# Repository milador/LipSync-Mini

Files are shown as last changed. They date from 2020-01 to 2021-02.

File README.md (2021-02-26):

# LipSync-Mini

Lipsync with updated electronics (Adafruit ItsyBitsy and RGB LED)

<p align="center">
LipSync Logo
</p>

The LipSync is an assistive technology device developed by <a href="https://www.makersmakingchange.com/" download target="_blank">MakersMakingChange</a> (An initiative by the <a href="https://www.neilsquire.ca/" download target="_blank">Neil Squire Society</a>) which allows quadriplegics and other people with limited hand use the ability to use touchscreen mobile devices by manipulation of a mouth-operated joystick with integrated sip and puff controls. 

<p align="center">
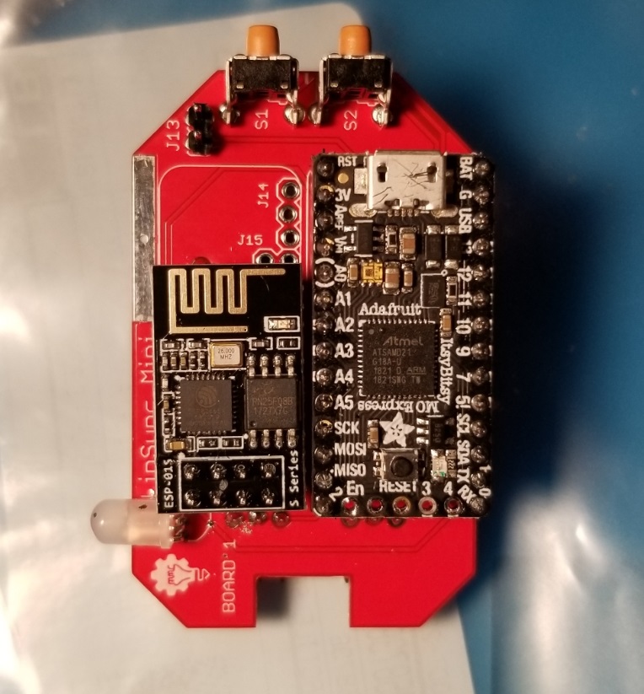
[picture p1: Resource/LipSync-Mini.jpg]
LipSync Logo

</p>

## Main LipSync github repository 

The LipSync Mini project is based on the <a href="https://github.com/makersmakingchange/LipSync" download target="_blank">LipSync</a>

## Changes Made

1. Dual color Led replaced by RGB addressable 
2. Arduino Micro replaced by Adafruit ItsyBitsy M0 (More memory and power)
3. Transistor and header pins for bluetooth module removed 
4. ItsyBitsy nRF52840 Express with bluetooth 5.0 is used for bluetooth version (Adafruit ItsyBitsy M0 replaced by ItsyBitsy nRF52840 Express)
5. Option to add ESP8266 Wifi Module to enable controlling IOT devices 
6. Option to add internal battery charger
7. Option to use internal input 3.5mm jack switch 
8. Option to replace sip and puff module with bite switch PCB

## License 

### MIT License

Copyright (c) 2020 Milador

Permission is hereby granted, free of charge, to any person obtaining a copy of this software and associated documentation files (the "Software"), to deal in the Software without restriction, including without limitation the rights to use, copy, modify, merge, publish, distribute, sublicense, and/or sell copies of the Software, and to permit persons to whom the Software is furnished to do so, subject to the following conditions:

The above copyright notice and this permission notice shall be included in all copies or substantial portions of the Software.

THE SOFTWARE IS PROVIDED "AS IS", WITHOUT WARRANTY OF ANY KIND, EXPRESS OR IMPLIED, INCLUDING BUT NOT LIMITED TO THE WARRANTIES OF MERCHANTABILITY, FITNESS FOR A PARTICULAR PURPOSE AND NONINFRINGEMENT. IN NO EVENT SHALL THE AUTHORS OR COPYRIGHT HOLDERS BE LIABLE FOR ANY CLAIM, DAMAGES OR OTHER LIABILITY, WHETHER IN AN ACTION OF CONTRACT, TORT OR OTHERWISE, ARISING FROM, OUT OF OR IN CONNECTION WITH THE SOFTWARE OR THE USE OR OTHER DEALINGS IN THE SOFTWARE.

<p align="center">
MIT License
</p>

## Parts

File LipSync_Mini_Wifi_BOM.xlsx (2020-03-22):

Qty | Component | Component name (August 12, 2019) | Manufacturer | COO | MPN | SKU | SKU | SKU | SKU | SKU | SKU | SKU | SKU | URL ( Canada ) | URL ( United States )
 |  |  |  |  |  | Digi-Key | Mouser | Qosina | Cole-Parmer | Lee Spring | U.S. Plastic Corp. | B&H Photo | Amazon
1 | Required | ItsyBitsy M0 Express | Adafruit Industries LLC | USA | "3727" | 1528-2554-ND | 485-3727 |  |  |  |  |  |  | https://www.digikey.ca/en/products/detail/adafruit-industries-llc/3727/8346575 | https://www.digikey.com/product-detail/en/arduino/A000053/1050-1066-ND
1 | Required | ESP8266 Wifi Module | SparkFun Electronics | USA | WRL-13678 | 1568-1235-ND |  |  |  |  |  |  |  | https://www.digikey.ca/product-detail/en/sparkfun-electronics/WRL-13678/1568-1235-ND/
1 | Required | 8 Position Header Connector Through Hole | Sullins | Taiwan | PPPC042LFBN-RC | S7107-ND |  |  |  |  |  |  |  | https://www.digikey.ca/product-detail/en/sullins-connector-solutions/PPPC042LFBN-RC/S7107-ND
2 | Required | Right Angle Push Button | Würth Elektronik | China | "431256058736" | 431256058736-ND |  |  |  |  |  |  |  | http://www.digikey.ca/product-detail/en/wurth-electronics-inc/431256058736/431256058736-ND | https://www.digikey.com/product-detail/en/wurth-electronics-inc/431256058736/431256058736-ND
4 | Required | 10k Ohm 1/4W Mini Axial Through-Hole Resistor | Stackpole Electronics | China | CFM14JT10K0 | S10KQCT-ND |  |  |  |  |  |  |  | https://www.digikey.ca/product-detail/en/stackpole-electronics-inc/CFM14JT10K0/S10KQCT-ND/ | https://www.digikey.com/product-detail/en/stackpole-electronics-inc/CFM14JT10K0/S10KQCT-ND/
1 | Required | Pressure Transducer | NXP Semiconductors | Malaysia | MP3V5010DP | MP3V5010DP-ND | 841-MP3V5010DP |  |  |  |  |  |  | https://www.digikey.ca/product-detail/en/nxp-usa-inc/MP3V5010DP/MP3V5010DP-ND | https://www.digikey.com/product-detail/en/freescale-semiconductor-nxp/MPXV7002DPT1/MPXV7002DPT1CT-ND
1 | Required | 0.01 uF Ceramic Through-Hole Radial Capacitor | KEMET | Mexico | C315C103K5R5TA | 399-4148-ND | 80-C315C103K5R |  |  |  |  |  |  | http://www.digikey.ca/product-detail/en/kemet/C315C103K5R5TA7303/399-9858-1-ND | http://www.digikey.com/product-detail/en/kemet/C315C103K5R5TA7303/399-9858-1-ND
1 | Required | 1.0 uF Ceramic Through-Hole Radial Capacitor | KEMET | Mexico | C315C105K3R5TA | 399-9714-ND | 80-C315C105K3R |  |  |  |  |  |  | http://www.digikey.ca/product-detail/en/kemet/C315C105K3R5TA/399-9714-ND | http://www.digikey.com/product-detail/en/kemet/C315C105K3R5TA/399-9714-ND
1 | Required | 470 pF Ceramic Through-Hole Radial Capacitor | KEMET | Mexico | C315C471K5R5TA | 399-9740-ND | 80-C315C471K5R |  |  |  |  |  |  | http://www.digikey.ca/product-detail/en/kemet/C315C471K5R5TA/399-9740-ND | http://www.digikey.com/product-detail/en/kemet/C315C471K5R5TA/399-9740-ND
2 | Required | 14-Position Straight Female Through-Hole Headers | Sullins | Taiwan | PPPC141LFBN-RC | S7047-ND |  |  |  |  |  |  |  | https://www.digikey.ca/product-detail/en/sullins-connector-solutions/PPPC141LFBN-RC/S7047-ND | http://www.digikey.com/product-detail/en/sullins-connector-solutions/PPPC171LFBN-RC/S7050-ND
2 | Required | 3-Position Right Angle Male Through-Hole Header | Molex | Mexico | 22-05-2031 | WM4101-ND |  |  |  |  |  |  |  | https://www.digikey.ca/product-detail/en/molex-connector-corporation/22-05-2031/WM4101-ND/ | https://www.digikey.com/product-detail/en/molex-connector-corporation/22-05-2031/WM4101-ND/ (https://www.digikey.ca/product-detail/en/molex-connector-corporation/22-05-2031/WM4101-ND/)
2 | Required | 3-Position Straight Female Through-Hole Header | Preci-Dip | Switzerland | 801-87-003-10-001101 | 1212-1180-ND |  |  |  |  |  |  |  | https://www.digikey.ca/product-detail/en/preci-dip/801-87-003-10-001101/1212-1180-ND | https://www.digikey.com/product-detail/en/preci-dip/801-87-003-10-001101/1212-1180-ND (https://www.digikey.ca/product-detail/en/preci-dip/801-87-003-10-001101/1212-1180-ND)
2 | Required | 4-Position Straight Female Through-Hole Header | Sullins | Taiwan | PPPC041LFBN-RC | S7037-ND |  |  |  |  |  |  |  | http://www.digikey.ca/product-detail/en/sullins-connector-solutions/PPPC041LFBN-RC/S7037-ND | https://www.digikey.com/product-detail/en/sullins-connector-solutions/PPPC041LFBN-RC/S7037-ND
1 | Required | 40-Position Breakaway Straight Male Through-Hole Headers | Sullins | Taiwan | PRPC040SAAN-RC | S1011EC-40-ND |  |  |  |  |  |  |  | http://www.digikey.ca/product-detail/en/sullins-connector-solutions/PRPC040SAAN-RC/S1011EC-40-ND | http://www.digikey.com/product-detail/en/sullins-connector-solutions/PRPC040SAAN-RC/S1011EC-40-ND
1 | Required | Addressable Lighting - 5 LED Discrete Serial | SparkFun Electronics | USA | COM-12986 | 1568-1213-ND |  |  |  |  |  |  |  | https://www.digikey.ca/en/products/detail/sparkfun-electronics/COM-12986/5673799 | https://www.digikey.com/product-detail/en/everlight-electronics-co-ltd/MV5437/1080-1109-ND/2675601 (https://www.digikey.ca/product-detail/en/everlight-electronics-co-ltd/MV5437/1080-1109-ND/2675600)
1 | Required | Jumper Shunt Connector | Sullins | Taiwan | SSC02SYAN | S9002-ND |  |  |  |  |  |  |  | https://www.digikey.ca/product-detail/en/sullins-connector-solutions/SPC02SYAN/S9002-ND | https://www.digikey.com/product-detail/en/sullins-connector-solutions/SPC02SYAN/S9002-ND (https://www.digikey.ca/product-detail/en/sullins-connector-solutions/SPC02SYAN/S9002-ND)
1 | Required | 6-Position Straight Female Through-Hole Header | Sullins | Taiwan | PPPC061LFBN-RC | S7039-ND |  |  |  |  |  |  |  | https://www.digikey.ca/product-detail/en/sullins-connector-solutions/PPPC061LFBN-RC/S7039-ND | https://www.digikey.com/product-detail/en/sullins-connector-solutions/PPPC061LFBN-RC/S7039-ND (https://www.digikey.ca/product-detail/en/sullins-connector-solutions/PPPC061LFBN-RC/S7039-ND)
1 | Required | Sip and Puff Mouthpiece | Qosina | USA | "80102" |  |  | "80102" |  |  |  |  |  | https://www.qosina.com/stepped-male-luer-lock-connector-80102 | https://www.qosina.com/stepped-male-luer-lock-connector-80102
1 | Required | Filter PTFE Hydrophobic 17 mm, 0.2 Micron | Qosina | USA | "28213" |  |  | "28213" |  |  |  |  |  | http://www.qosina.com/hydrophobic-filter-with-female-luer-lock-inlet-male-luer-lock-outlet-28213 | http://www.qosina.com/hydrophobic-filter-with-female-luer-lock-inlet-male-luer-lock-outlet-28213
1 | Required | Luer Lock Fitting | Cole-Parmer | USA | RK-45508-32 |  |  |  | RK-45508-32 |  |  |  |  | https://www.coleparmer.ca/i/cole-parmer-female-luer-bulkhead-1-4-28-unf-thread-to-3-32-hose-barb-pp-25-pk/4550832 | https://www.coleparmer.ca/i/cole-parmer-female-luer-bulkhead-1-4-28-unf-thread-to-3-32-hose-barb-pp-25-pk/4550832
4 | Required | Force Resistive Sensor | Interlink Electronics | China | 30-49649 | 1027-1000-ND |  |  |  |  |  |  |  | http://www.digikey.ca/product-detail/en/interlink-electronics/30-49649/1027-1000-ND | http://www.digikey.com/product-detail/en/interlink-electronics/30-49649/1027-1000-ND
4 | Required | Screws Phillips Head M3 | Essentra Components | Taiwan | NMS-308 | RP809-ND |  |  |  |  |  |  |  | https://www.digikey.ca/product-detail/en/essentra-components/NMS-308/RP809-ND | https://www.digikey.com/product-detail/en/essentra-components/NMS-308/RP809-ND (https://www.digikey.ca/product-detail/en/essentra-components/NMS-308/RP809-ND)
6 | Required | Compression Spring | Lee Spring | China | LC 016C 03 S |  |  |  |  | LC 016C 03 S |  |  |  | https://www.leespring.com/compression-springs?search=LC016C03S | https://www.leespring.com/compression-springs?search=LC016C03S
2 | Required | Standoff M3 10mm | Keystone | USA | "25501" | 36-25501-ND | 534-25501 |  |  |  |  |  |  | http://www.digikey.ca/product-detail/en/keystone-electronics/25501/36-25501-ND/ | http://www.digikey.com/product-detail/en/keystone-electronics/25501/36-25501-ND/
2 | Required | Standoff M3 15mm | Keystone | USA | "25503" | 36-25503-ND | 534-25503 |  |  |  |  |  |  | http://www.digikey.ca/product-detail/en/keystone-electronics/25503/36-25503-ND/ | http://www.digikey.com/product-detail/en/keystone-electronics/25503/36-25503-ND/ (http://www.digikey.ca/product-detail/en/keystone-electronics/25503/36-25503-ND/)
1 | Required | Luer Lock Nut | Cole-Parmer | USA | 45509-04 |  |  |  | 45509-04 |  |  |  |  | https://www.coleparmer.ca/i/cole-parmer-panel-mount-lock-nut-1-4-28-unf-black-nylon-25-pk/4550904 | https://www.coleparmer.ca/i/cole-parmer-panel-mount-lock-nut-1-4-28-unf-black-nylon-25-pk/4550904
4 | Required | Bumper | 3M | USA | SJ-5003 (BLACK) | SJ5003-0-ND | 517-SJ-5003BK |  |  |  |  |  |  | https://www.mouser.ca/ProductDetail/3M-Electronic-Specialty/SJ-5003-BLACK?qs=sGAEpiMZZMvlOED0T0kTWubpGv7E7tyx | https://www.digikey.com/product-detail/en/3m/SJ-5003-(BLACK)/SJ5003-0-ND/102574 (https://www.digikey.ca/product-detail/en/3m/SJ-5003-(BLACK)/SJ5003-0-ND/102573)
4 | Required | Nut M3 | Keystone Electronics | Taiwan | 4708 | 36-4708-ND |  |  |  |  |  |  |  | https://www.digikey.ca/product-detail/en/keystone-electronics/4708/36-4708-ND/4499301 | https://www.digikey.com/product-detail/en/keystone-electronics/4708/36-4708-ND/4499301
1 | Required | Tubing Tygon 3350 3/32" ID x 45mm | Tygon® | USA | "57289" |  |  |  |  |  | "57289" |  |  | http://www.usplastic.com/catalog/item.aspx?itemid=31562&catid=864 | http://www.usplastic.com/catalog/item.aspx?itemid=31562&catid=864
1 | Required | Light Pipe | Dialight | Malaysia | 51513030250F | 350-3746-ND | 645-515-1303-0250F |  |  |  |  |  |  | http://www.mouser.com/search/ProductDetail.aspx?r=645-515-1303-0250F | http://www.mouser.com/search/ProductDetail.aspx?r=645-515-1303-0250F
1 | Required | Threaded Insert 5/8”-27 | WindTech | USA | M-11 |  |  |  |  |  |  | WIM11 |  | https://www.bhphotovideo.com/c/product/850285-REG/windtech_m_11_5_8_27_f_to_1_2_m_npt.html | https://www.adorama.com/wtm11.html
1 | Required | Threaded Adapter 5/8"-27 | CAMVATE | China | Mic Adapter |  |  |  |  |  |  |  | Mic Adapter | https://www.amazon.com/CAMVATE-Female-Male-Piece-Adapter/dp/B01GWVQ022 | https://www.amazon.com/CAMVATE-Female-Male-Piece-Adapter/dp/B01GWVQ022
1 | Required | USB Cable 3' or 6' | Startech | China | UUSBHAUB3RA |  |  |  |  |  |  |  | USB Cable 3' or 6' | https://www.amazon.ca/Startech-Com-UUSBHAUB3RA-Micro-Cable-Right/dp/B001AR4NC8 | https://www.amazon.com/StarTech-com-Micro-USB-Cable-UUSBHAUB3RA/dp/B001AR4NC8 | https://www.amazon.com/gp/huc/view.html?ie=UTF8&newItems=C50dc2962-6371-4880-bf41-06ac5db860d9%2C1 | https://www.amazon.com/gp/product/B01M18TDO1/ref=ox_sc_act_title_2?smid=A21TE5CLHZDYA7&psc=1
1 | Required | USB Splitter | JIUWU | China | USB Splitter |  |  |  |  |  |  |  | USB Splitter | https://www.amazon.ca/Wpeng-Female-degree-Micro-Splitter/dp/B01M5F47SY | https://www.amazon.com/Micro-Female-Cable-Power-Splitter/dp/B00NSBVNCM
1 | Required | Cable Tie | Panduit Corp | Singapore | PLT.6SM-M |  | 644-PLT.6SM-M |  |  |  |  |  |  | https://www.mouser.ca/ProductDetail/Panduit/PLT6SM-M | https://www.mouser.com/ProductDetail/Panduit/PLT6SM-M
1 | Optional | Magic Arm 11" and Clamp | YKS / GkGk | China | ZC462800 |  |  |  |  |  |  |  | Magic Arm 11" and Clamp | https://www.amazon.com/GkGk-Articulating-Friction-Adjustable-Monitor/dp/B017HKJVL4/ | https://www.amazon.com/GkGk-Articulating-Friction-Adjustable-Monitor/dp/B017HKJVL4/
1 | Optional | 3.50mm Headphone Phone Jack Stereo | CUI Devices | USA | SJ1-3533NG | CP1-3533NG-ND |  |  |  |  |  |  |  | https://www.digikey.ca/product-detail/en/cui-devices/SJ1-3533NG/CP1-3533NG-ND
1 | Optional | MCP73831 Battery Board Power Management Pro | Adafruit Industries LLC | USA | "2124" | "1528-1443-ND" |  |  |  |  |  |  |  | https://www.digikey.ca/product-detail/en/adafruit-industries-llc/2124/1528-1443-ND
1 | Optional | 3-Position Straight Female Through-Hole Header | Sullins | Taiwan | PPPC031LFBN-RC | S7036-ND |  |  |  |  |  |  |  | https://www.digikey.ca/product-detail/en/sullins-connector-solutions/PPPC031LFBN-RC/S7036-ND
1 | Optional | 2-Position Straight Female Through-Hole Header | Sullins | Taiwan | PPPC021LFBN-RC | S7035-ND |  |  |  |  |  |  |  | https://www.digikey.ca/product-detail/en/sullins-connector-solutions/PPPC021LFBN-RC/S7035-ND
1 | Optional | 2-Position Straight Male Through-Hole Headers | Sullins | Taiwan | PRPC002SAAN-RC | S1011EC-02-ND |  |  |  |  |  |  |  | https://www.digikey.ca/product-detail/en/sullins-connector-solutions/PRPC002SAAN-RC/S1011EC-02-ND

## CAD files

Hardware/Housing_design/LipSync_Button.stl
6.00 x 19.3 x 8.00

Hardware/Housing_design/LipSync_Joystick_Stand.STL
48.0 x 79.3 x 41.0

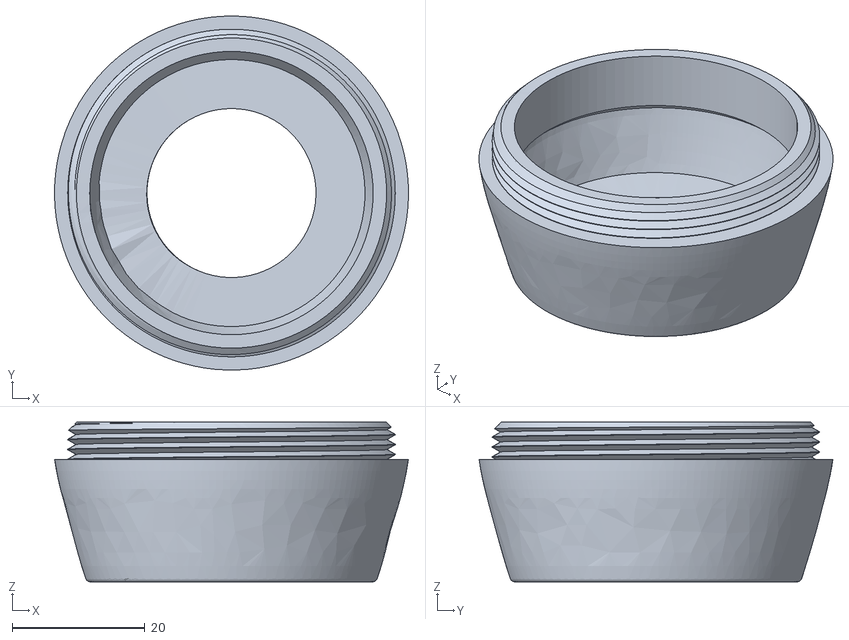
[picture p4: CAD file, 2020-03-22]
Hardware/Housing_design/LipSync_Front_Housing.STL
53.4 x 53.4 x 24.1

Hardware/Housing_design/LipSync_Joystick_Front.STL
40.0 x 39.9 x 5.50

Hardware/Housing_design/LipSync_Joystick_Base.STL
46.0 x 46.0 x 9.75

Hardware/Housing_design/LipSync_Joystick_Rocker.STL
40.0 x 40.0 x 4.00

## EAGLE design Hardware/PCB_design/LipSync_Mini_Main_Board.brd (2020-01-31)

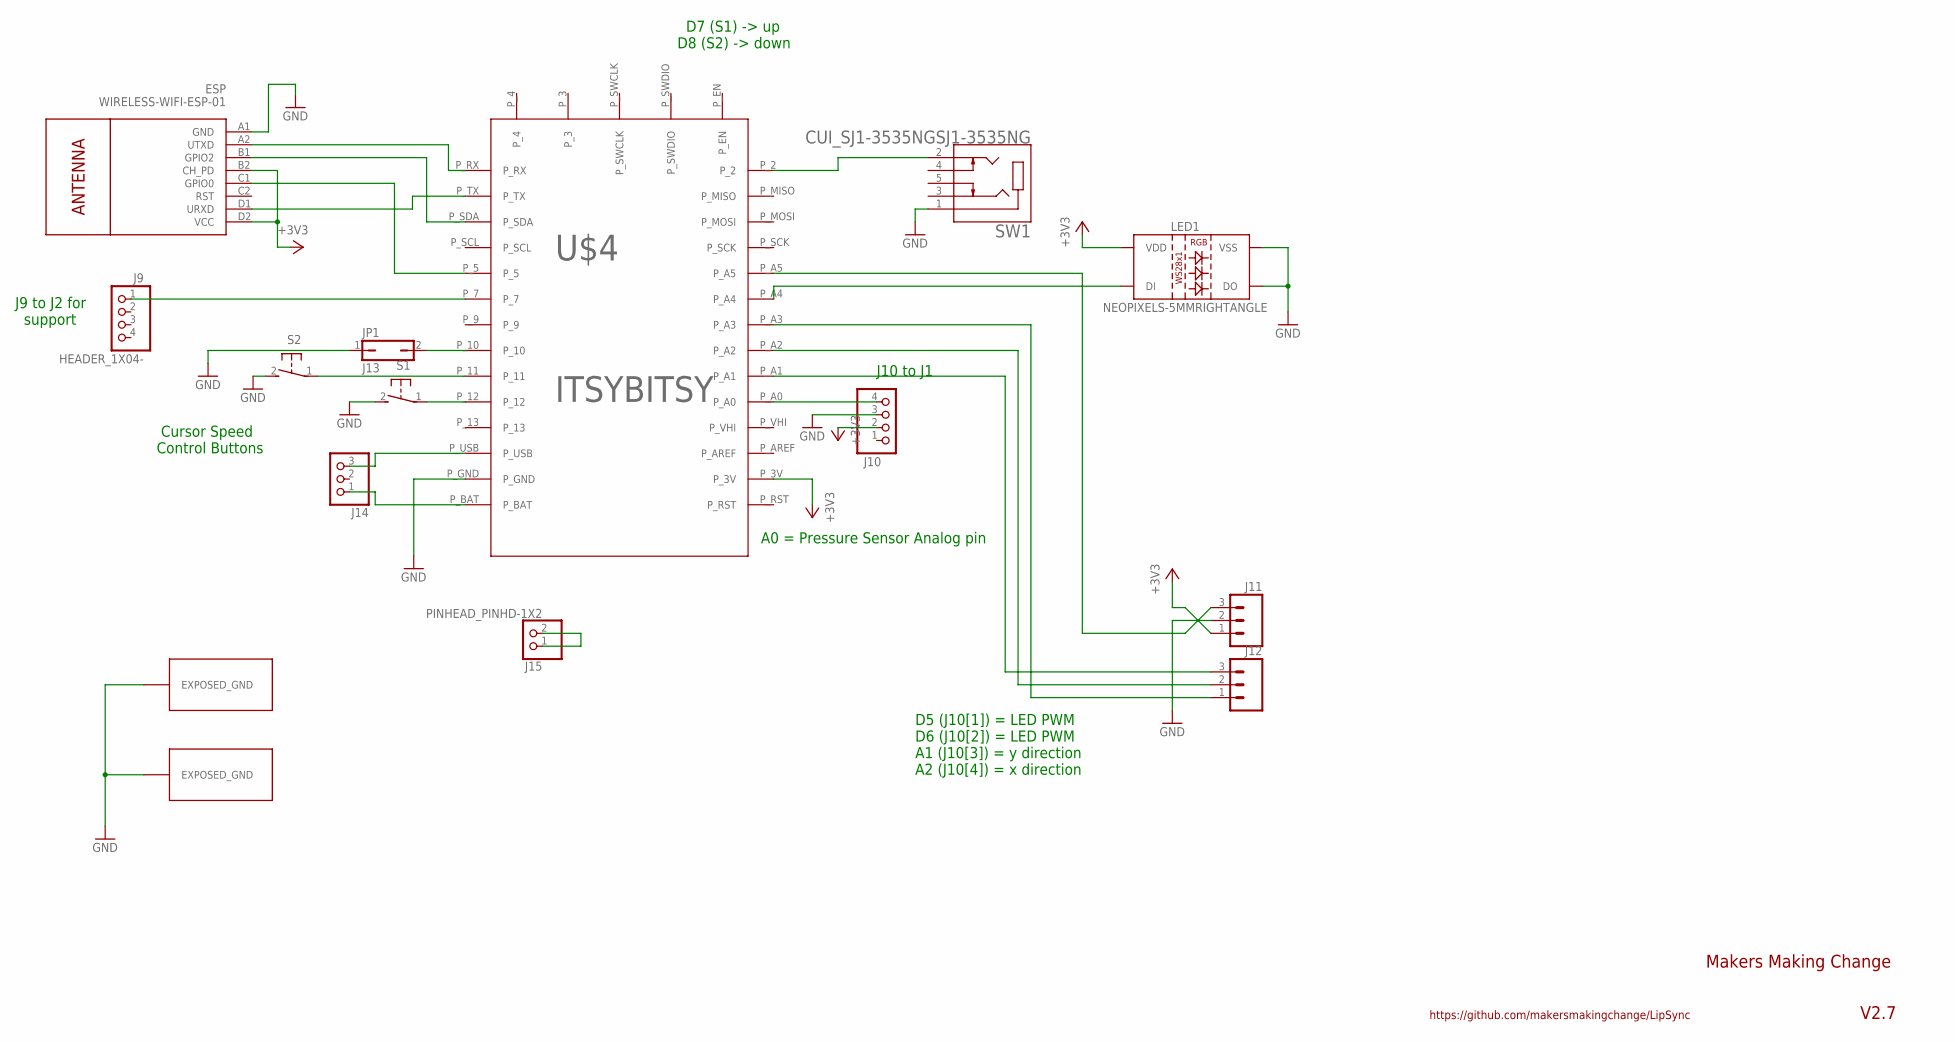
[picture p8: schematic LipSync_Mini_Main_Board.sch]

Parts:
ESP: WIRELESS-WIFI-ESP-01
J9, J10: HEADER_1X04-; 1X04
J11, J12: HEADER_1X03-/90; 1X03_LOCK/90
J13: JP1
J14: PINHEAD_PINHD-1X3; PINHEAD_1X03
J15: PINHEAD_PINHD-1X2; PINHEAD_1X02
LED1: NEOPIXELS-5MMRIGHTANGLE; NEOPIXELS-RIGHTANGLE-5MM
S1, S2: B3F_31-XXSKINNY; B3F-31XX-SKINNIER
SW1: CUI_SJ1-3535NGSJ1-3535NG; CUI_SJ1-3535NG
U$2, U$3: EXPOSED_GND
U$4: ITSYBITSY

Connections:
+3V3: ESP.B2 (CH_PD), ESP.D2 (VCC), J10.2, J11.1, LED1.P2 (VDD), U$4.P_3V
GND: ESP.A1 (GND), J10.3, J11.2, J13.1, LED1.P3 (VSS), LED1.P4 (DO), S1.2 (S), S2.2 (S), SW1.1, U$2.GND1, U$3.GND1, U$4.P_GND
unnamed: S1.1, U$4.P_12
unnamed: S2.1, U$4.P_11
unnamed: J13.2, U$4.P_10
unnamed: LED1.P1 (DI), U$4.P_A4
unnamed: J12.3, U$4.P_A1
unnamed: J12.2, U$4.P_A2
unnamed: ESP.D1 (URXD), U$4.P_TX
unnamed: ESP.A2 (UTXD), U$4.P_RX
unnamed: ESP.B1 (GPIO2), U$4.P_SDA
unnamed: J11.3, U$4.P_A5
unnamed: J10.4, U$4.P_A0
unnamed: J14.3, U$4.P_USB
unnamed: J14.1, U$4.P_BAT
unnamed: ESP.C1 (GPIO0), U$4.P_5
unnamed: SW1.2, U$4.P_2
unnamed: J12.1, U$4.P_A3
unnamed: J15.1, J15.2
unnamed: J9.1, U$4.P_7

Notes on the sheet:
J9 to J2 for support
D5 (J10[1]) = LED PWM D6 (J10[2]) = LED PWM A1 (J10[3]) = y direction A2 (J10[4]) = x direction
J10 to J1
Cursor Speed Control Buttons
D7 (S1) -> up D8 (S2) -> down
Makers Making Change
V2.7
https://github.com/makersmakingchange/LipSync
A0 = Pressure Sensor Analog pin

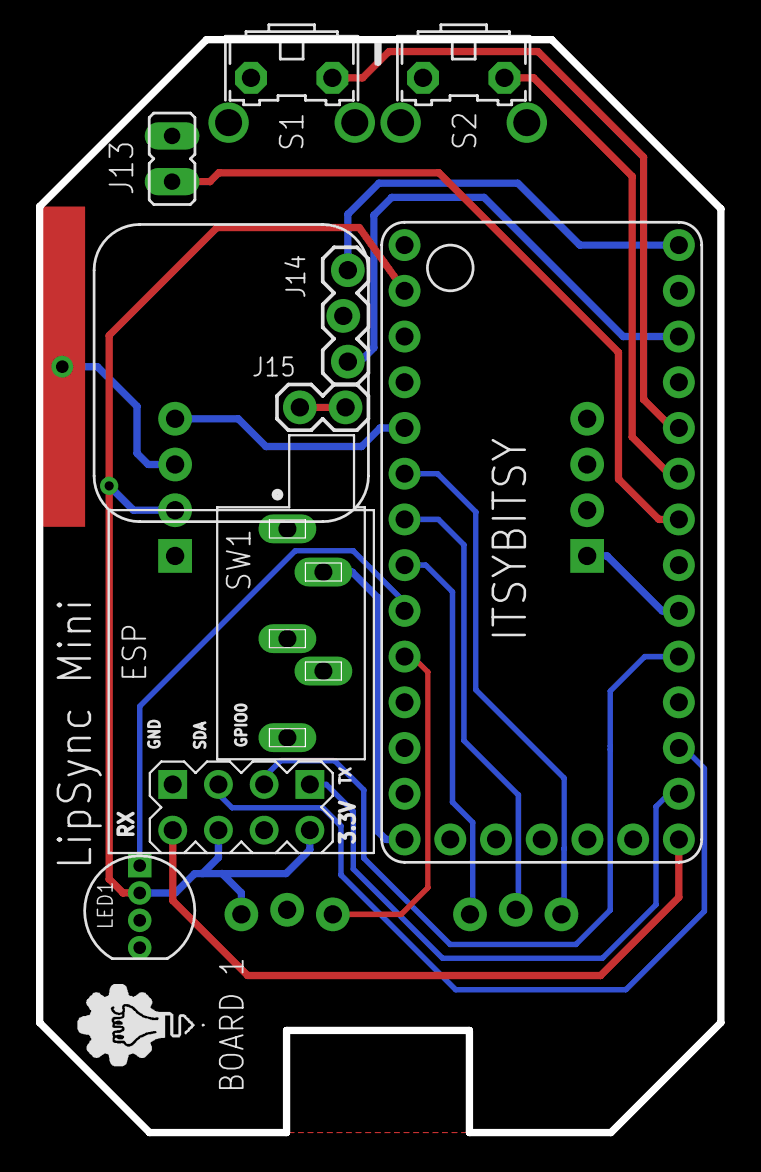
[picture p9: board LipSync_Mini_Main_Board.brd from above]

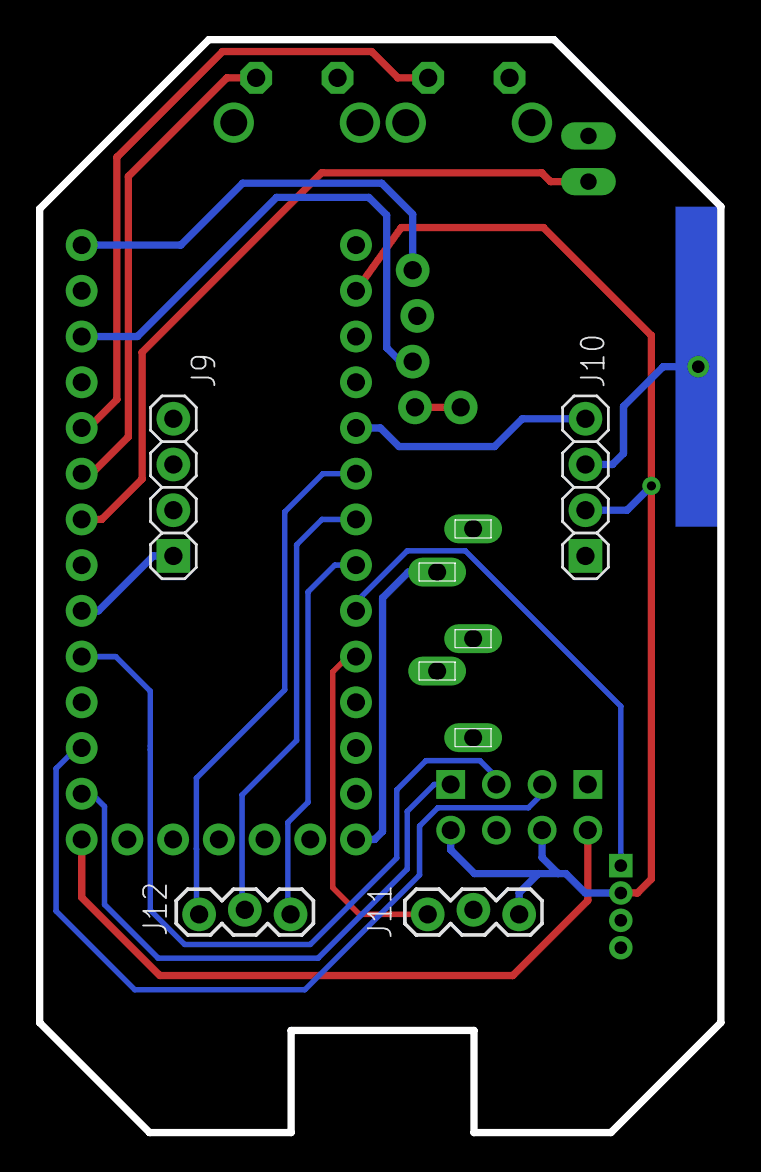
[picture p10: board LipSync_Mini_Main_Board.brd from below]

Board: 2 copper layers, 37.8 x 60.7 mm, 15 parts (5 on the bottom side), 20 nets.

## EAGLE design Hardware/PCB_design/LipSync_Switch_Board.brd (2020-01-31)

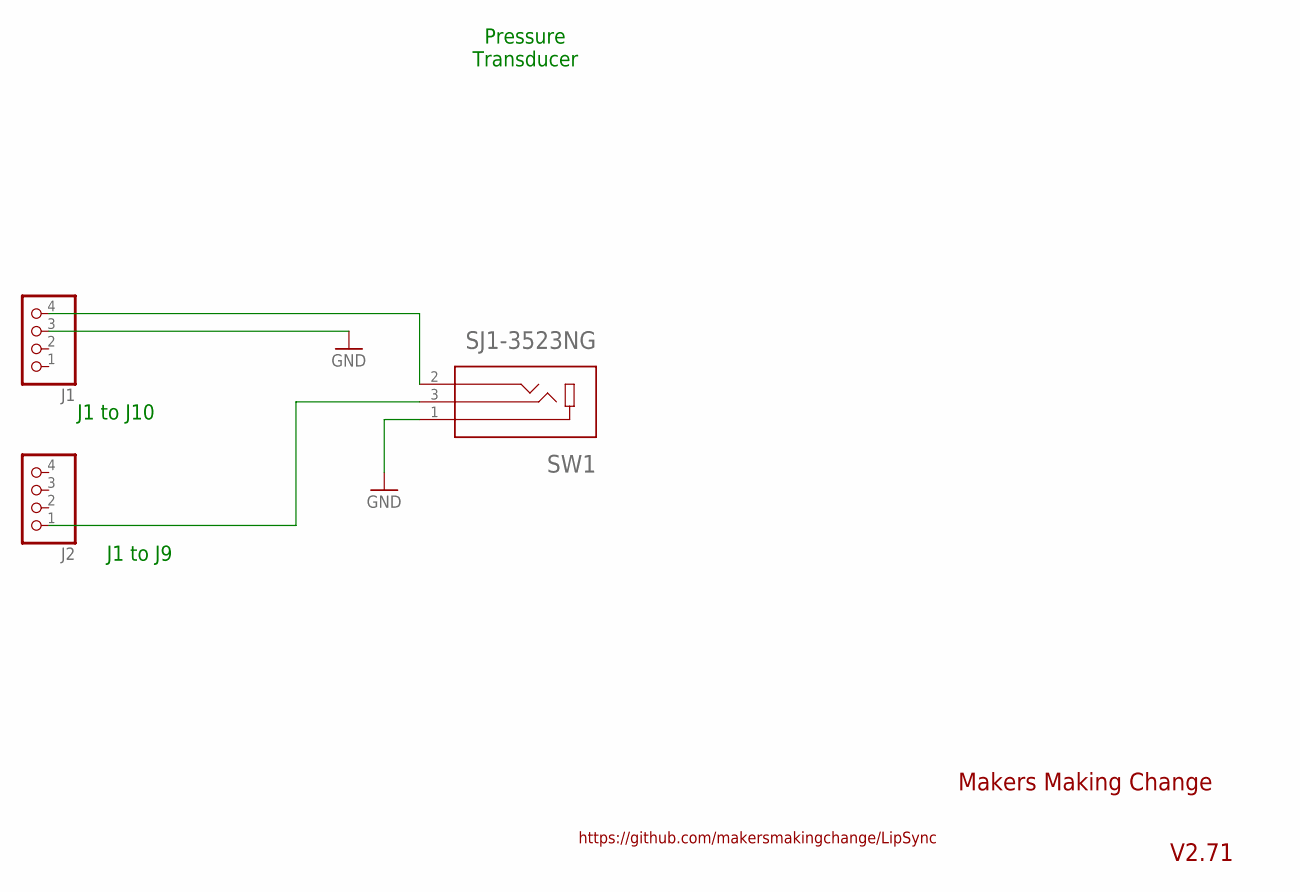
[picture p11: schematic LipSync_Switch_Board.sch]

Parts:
J1, J2: PINHEAD_PINHD-1X4; PINHEAD_1X04
SW1: SJ1-3523NG; CUI_SJ1-3523NG

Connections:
GND: J1.3, SW1.1
unnamed: J1.4, SW1.2
unnamed: J2.1, SW1.3

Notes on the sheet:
J1 to J10
Pressure Transducer
Makers Making Change
V2.71
https://github.com/makersmakingchange/LipSync
J1 to J9

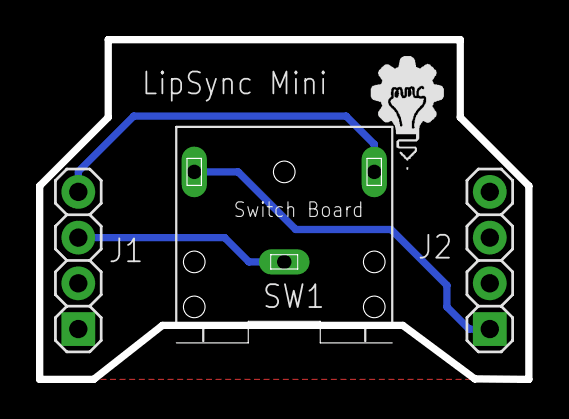
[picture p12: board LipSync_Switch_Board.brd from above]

Board: 2 copper layers, 27.2 x 18.9 mm, 3 parts (0 on the bottom side), 3 nets.

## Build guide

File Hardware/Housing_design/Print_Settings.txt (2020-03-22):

Print all components in orientation of STL file.

----------------------------
First print:
LipSync_Front_Housing
LipSync_Rear_Housing
LipSync_Button (2 are needed)
LipSync_Joystick_Stand

Infill: 20%
Layer Height: 0.2mm
Support Material: No
Raft: No
----------------------------

----------------------------
Second print:
LipSync_Joystick_Front_Plate
LipSync_Joystick_Rocker
LipSync_Joystick_Base

Infill: 50%
Layer Height: 0.2mm
Support Material: Yes
Raft: No
----------------------------

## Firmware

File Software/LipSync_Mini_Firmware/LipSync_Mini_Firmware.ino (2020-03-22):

/*
//                                                                                                  
//  +++         .+++:    /++++++++/:.     .:/+++++/: .+++/`     .+++/  ++++.      ++++.     `-/++++++/:
//  oooo         .ooo:    +ooo:--:+ooo/   :ooo/:::/+/  -ooo+`   .ooo+`  ooooo:     .o-o`   `/ooo+//://+:
//  oooo         .ooo:    +ooo`    :ooo-  oooo`     `   .ooo+` .ooo+`   oooooo/`   .o-o`  .oooo-`       
//  oooo         .ooo:    +ooo`    -ooo-  -ooo+:.`       .ooo+.ooo/`    ooo:/oo+.  .o-o`  +ooo.         
//  oooo         .ooo:    +ooo.`..:ooo+`   `:+oooo+:`     `+ooooo/      ooo: :ooo- .o-o`  oooo          
//  oooo         .ooo:    +ooooooooo+:`       `-:oooo-     `+ooo/       ooo/  .+oo/.o-o`  +ooo.         
//  oooo         .ooo:    +ooo-...``             `oooo      /ooo.       ooo/   `/oo-o-o`  .oooo-        
//  oooo::::::.  .ooo:    +ooo`           :o//:::+ooo:      /ooo.       ooo/     .o-o-o`   ./oooo/:::/+/
//  +ooooooooo:  .ooo:    /ooo`           -/++ooo+/:.       :ooo.       ooo:      `.o.+      `-/+oooo+/-
//
//An assistive technology device which is developed to allow quadriplegics to use touchscreen mobile devices by manipulation of a mouth-operated joystick with integrated sip and puff controls.
*/

//Developed by : MakersMakingChange
//Modified by: Milad Hajihassan
//Firmware : LipSync_Mini_Firmware
//VERSION: 1.0 (21 March 2020) 



#include "Mouse.h"
//#include <StopWatch.h>
#include <Adafruit_NeoPixel.h>
#include <FlashAsEEPROM.h>
#include <math.h>

//***INPUT/OUTPUT PIN CONFIGURATION***//


#define BUTTON_UP_PIN 12                           // Cursor Control Button 1: UP - digital input pin 12 (internally pulled-up)
#define BUTTON_DOWN_PIN 11                         // Cursor Control Button 2: DOWN - digital input pin 11 (internally pulled-up)
#define LED_PIN A4                               // LipSync RGB LED : analog output pin A4

#define PIO4_PIN 10                               // PIO4_PIN Command Pin - digital output pin 10

#define X_DIR_HIGH_PIN A2                         // X Direction High (Cartesian positive x : right) - analog input pin A2
#define X_DIR_LOW_PIN A3                          // X Direction Low (Cartesian negative x : left) - analog output pin A3
#define Y_DIR_HIGH_PIN A5                         // Y Direction High (Cartesian positive y : up) - analog input pin A5
#define Y_DIR_LOW_PIN A1                         // Y Direction Low (Cartesian negative y : down) - analog input pin A1
#define PRESSURE_PIN A0                           // Sip & Puff Pressure Transducer Pin - analog input pin A0

//***CUSTOMIZE VALUES***//

#define PRESSURE_THRESHOLD 0.4                    //puff threshold 
#define DEBUG_MODE true                           //Debug mode ( Enabled = true and Disabled = false )
#define CURSOR_DEFAULT_SPEED 30                   //Maximum default USB cursor speed                  
#define CURSOR_DELTA_SPEED 5                      //Delta value that is used to calculate USB cursor speed levels
#define CURSOR_RADIUS 50.0                        //Constant joystick radius
#define LED_BRIGHTNESS 125                         //The mode led color brightness

//***VARIABLE DECLARATION***//

int cursorSpeedCounter = 5;                       //Cursor speed counter which is set to 4 by default 


int xHigh, yHigh, xLow, yLow;                       
int xRight, xLeft, yUp, yDown;                    //Individual neutral starting positions for each FSR

int xHighMax, xLowMax, yHighMax, yLowMax;         //Max FSR values which are set to the values from EEPROM


float xHighYHighRadius, xHighYLowRadius, xLowYLowRadius, xLowYHighRadius;
float xHighYHigh, xHighYLow, xLowYLow, xLowYHigh;

int cursorDeltaBox;                               //The delta value for the boundary range in all 4 directions about the x,y center
int cursorDelta;                                  //The amount cursor moves in some single or combined direction
int cursorClickStatus = 0;                        //The value indicator for click status, ie. tap, back and drag ( example : 0 = tap )
int configDone;                                   // Binary check of completed configuration
unsigned int puffCount, sipCount;                 //The puff and long sip incremental counter variables
int pollCounter = 0;                              //Cursor poll counter

int cursorDelay;
float cursorFactor;
int cursorMaxSpeed;

float yHighComp = 1.0;
float yLowComp = 1.0;
float xHighComp = 1.0;
float xLowComp = 1.0;

float yHighDebug, yLowDebug, xHighDebug, xLowDebug;
int yHighMaxDebug, yLowMaxDebug, xHighMaxDebug, xLowMaxDebug;

//Pressure sensor variables
float sipThreshold, puffThreshold, cursorClick;

//RGB LED Color code structure 

struct rgbColorCode {
    int r;    // red value 0 to 255
    int g;   // green value
    int b;   // blue value
 };

//Color structure 
typedef struct { 
  uint8_t colorNumber;
  String colorName;
  rgbColorCode colorCode;
} colorStruct;

//Color properties 
const colorStruct colorProperty[] {
    {1,"GREEN",{0,100,0}},
    {2,"PINK",{100,0,40}},
    {3,"YELLOW",{100,100,0}},    
    {4,"ORANGE",{100,40,0}},
    {5,"BLUE",{0,0,100}},
    {6,"RED",{100,0,0}},
    {7,"PURPLE",{100,0,100}},
    {8,"TEAL",{0,128,128}}       
};

//Action structure 
typedef struct { 
  uint8_t actionNumber;
  String actionName;
  uint8_t actionColorNumber;
} actionStruct;

//Action properties 
const actionStruct actionProperty[] {
    {0,"Initialization",8},
    {1,"Calibration",5},
    {2,"Calibration_Start",1},
    {3,"Calibration_End",6},
    {4,"Calibration_Home",5},
    {5,"Swipe",3},
    {6,"Scroll",3},
    {7,"Speed_Increase",1},
    {8,"Speed_Decrease",6},
    {9,"Speed_Max",3}
};

//Cursor Speed Level structure 
typedef struct {
  int _delay;
  float _factor;
  int _maxSpeed;
} _cursor;

//Define characteristics of each speed level ( Example: 5,-1.0,10)
_cursor setting1 = {5, -1.1, CURSOR_DEFAULT_SPEED - (5 * CURSOR_DELTA_SPEED)};
_cursor setting2 = {5, -1.1, CURSOR_DEFAULT_SPEED - (4 * CURSOR_DELTA_SPEED)};
_cursor setting3 = {5, -1.1, CURSOR_DEFAULT_SPEED - (3 * CURSOR_DELTA_SPEED)};
_cursor setting4 = {5, -1.1, CURSOR_DEFAULT_SPEED - (2 * CURSOR_DELTA_SPEED)};
_cursor setting5 = {5, -1.1, CURSOR_DEFAULT_SPEED - (CURSOR_DELTA_SPEED)};
_cursor setting6 = {5, -1.1, CURSOR_DEFAULT_SPEED};
_cursor setting7 = {5, -1.1, CURSOR_DEFAULT_SPEED + (CURSOR_DELTA_SPEED)};
_cursor setting8 = {5, -1.1, CURSOR_DEFAULT_SPEED + (2 * CURSOR_DELTA_SPEED)};
_cursor setting9 = {5, -1.1, CURSOR_DEFAULT_SPEED + (3 * CURSOR_DELTA_SPEED)};
_cursor setting10 = {5, -1.1, CURSOR_DEFAULT_SPEED + (4 * CURSOR_DELTA_SPEED)};
_cursor setting11 = {5, -1.1, CURSOR_DEFAULT_SPEED + (5 * CURSOR_DELTA_SPEED)};

_cursor cursorParams[11] = {setting1, setting2, setting3, setting4, setting5, setting6, setting7, setting8, setting9, setting10, setting11};

int single = 0;
int puff1, puff2;

bool settingsEnabled = false; 

//Declare the RGB LED's
Adafruit_NeoPixel ledPixel = Adafruit_NeoPixel(1, LED_PIN, NEO_GRB + NEO_KHZ800);

float pressure_test;

//-----------------------------------------------------------------------------------//

//***MICROCONTROLLER AND PERIPHERAL MODULES CONFIGURATION***//

void setup() {
  
  Serial.begin(115200);                           //Setting baud rate for serial communication which is used for diagnostic data returned from Bluetooth and microcontroller

  pinMode(LED_PIN, OUTPUT);                       //Set the LED pin 1 as output(GREEN LED)
  pinMode(PRESSURE_PIN, INPUT);                   //Set the pressure sensor pin input
  pinMode(X_DIR_HIGH_PIN, INPUT);                 //Define Force sensor pinsas input ( Right FSR )
  pinMode(X_DIR_LOW_PIN, INPUT);                  //Define Force sensor pinsas input ( Left FSR )
  pinMode(Y_DIR_HIGH_PIN, INPUT);                 //Define Force sensor pinsas input ( Up FSR )
  pinMode(Y_DIR_LOW_PIN, INPUT);                  //Define Force sensor pinsas input ( Down FSR )


  pinMode(BUTTON_UP_PIN, INPUT_PULLUP);           //Set increase cursor speed button pin as input
  pinMode(BUTTON_DOWN_PIN, INPUT_PULLUP);         //Set decrease cursor speed button pin as input

  pinMode(2, INPUT_PULLUP);                       //Set unused pins as inputs with pullups
  pinMode(3, INPUT_PULLUP);
  pinMode(4, INPUT_PULLUP);
  pinMode(7, INPUT_PULLUP);
  pinMode(9, INPUT_PULLUP);
  pinMode(13, INPUT_PULLUP);


  //while(!Serial1);
  delay(2000);
  joystickInitialization();                       //Set the Home joystick and generate movement threshold boundaries
  delay(10);
  pressureSensorInitialization();                 //Set the pressure sensor threshold boundaries
  delay(10);

  
  setDefault();                                   //Set the default values that are stored in EEPROM
  delay(10);
  mouseConfigure();                               //Configure the HID mouse functions
  delay(10);
  usbConfigure();                                 //USB configuration 
  delay(10);
  readCursorSpeed();                              //Read the saved cursor speed parameter from EEPROM
  delay(10);
  initLed(LED_BRIGHTNESS);                        //RGB Led's initialization 
  delay(10);
  displayVersion();                               //Display firmware version number
  delay(10);
  initLedFeedback();                              //Show led feedback that the device is ready to use and indicate current mode
  delay(10);
  forceCursorDisplay();                           //Display cursor on screen by moving it
  

  cursorDelay = cursorParams[cursorSpeedCounter]._delay;
  cursorFactor = cursorParams[cursorSpeedCounter]._factor;
  cursorMaxSpeed = cursorParams[cursorSpeedCounter]._maxSpeed;

  //Functions below are for diagnostic feedback only
  if(DEBUG_MODE==true) {
      puff1=EEPROM.read(0);
      delay(5);
      Serial.println((String)"configDone: "+puff1);
      delay(5);
      puff2=EEPROM.read(2);
      delay(5);
      Serial.println((String)"cursorSpeedCounter: "+puff2);
      delay(5);
      Serial.println((String)"cursorDelay: "+cursorParams[puff2]._delay);
      delay(5);
      Serial.println((String)"cursorFactor: "+cursorParams[puff2]._factor);
      delay(5);
      Serial.println((String)"cursorMaxSpeed: "+cursorParams[puff2]._maxSpeed);
      delay(5);
      yHighDebug=EEPROM.read(6);
      delay(5);
      Serial.println((String)"yHighComp: "+yHighDebug);
      delay(5);
      yLowDebug=EEPROM.read(10);
      delay(5);
      Serial.println((String)"yLowComp: "+yLowDebug);
      delay(5);
      xHighDebug=EEPROM.read(14);
      delay(5);
      Serial.println((String)"xHighComp: "+xHighDebug);
      delay(5);
      xLowDebug=EEPROM.read(18);
      delay(5);
      Serial.println((String)"xLowComp: "+xLowDebug);
      delay(5);
      xHighMaxDebug=EEPROM.read(22);
      delay(5);
      Serial.println((String)"xHighhMax: "+xHighMaxDebug);
      delay(5);
      xLowMaxDebug=EEPROM.read(24);
      delay(5);
      Serial.println((String)"xLowMax: "+xLowMaxDebug);
      delay(5);
      yHighMaxDebug=EEPROM.read(26);
      delay(5);
      Serial.println((String)"yHighMax: "+yHighMaxDebug);
      delay(5);
      yLowMaxDebug=EEPROM.read(28);
      delay(5);
      Serial.println((String)"yLowMax: "+yLowMaxDebug);
      delay(5);
  }
  
}

//-----------------------------------------------------------------------------------//

//***START OF MAIN LOOP***//
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

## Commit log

2020-01-31 Updated PCB design with Itsybitsy board, RGB led, ESP IOT connection and ability to switch pressure sensor with bite switch board
    [LipSync_Mini_Main_Board.brd, LipSync_Mini_Main_Board.sch, LipSync_Switch_Board.brd, LipSync_Switch_Board.sch]
2020-03-22 Added part list for 3 versions
    [LipSync_Mini_BOM.xlsx, LipSync_Mini_Bluetooth_BOM.xlsx, LipSync_Mini_Wifi_BOM.xlsx]
2020-03-22 Added enclosure 3D printing files
    [LipSync_Button.stl, LipSync_Front_Housing.STL, LipSync_Joystick_Base.STL, LipSync_Joystick_Front.STL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]
2020-03-22 Added sample picture
2020-03-22 Updated part list for wifi version
    [LipSync_Mini_Wifi_BOM.xlsx]

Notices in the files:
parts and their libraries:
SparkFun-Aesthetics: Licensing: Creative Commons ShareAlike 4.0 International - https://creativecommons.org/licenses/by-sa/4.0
